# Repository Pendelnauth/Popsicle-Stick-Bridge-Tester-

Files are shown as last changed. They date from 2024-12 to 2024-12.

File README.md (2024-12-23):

# Popsicle Stick Bridge Tester
This is a basic Popsicle Stick Bridge Tester designed for use in a classroom environment.

# Back Story

This project was created to easily test popsicle stick bridges that students created as a part of the curriculum. This allows a safer and more accurate testing method compared to other more traditional methods.

# Project Notes

Because this is a one-off project little effort was put into refining the project. Certain aspects of the project need manual modification to allow for working functionality.
  1. The onboard regulator for the -5V rail only can produce -3.3V due to being fed 3.3v and a misunderstanding in the datasheet. The fix for this was to simply change the resistors to set the output voltage to -3V. Because the -5V rail is used to excite the load cell the output voltage is slightly lower making it more difficult to measure.
  2. ADC 16x gain input impedance. Due to the small voltage needed to be measured the internal PGA of the ADC is used to help achieve more stable readings from the load cells. This causes the input impedance of the ADC to drop off rapidly resulting in skewed measurements. To fix this additional oversampling (ADC-based) was applied as well as a rolling average(Program based) while using a lower gain. This kept the visually present noise down to an acceptable level. The preferred solution would be to either use a dedicated buffer or general-purpose amp before the ADC to drive it even at the lower input impedances adequately. Or make use of a purpose-built load cell measurement IC. 

Make sure to check out the User Manual for additional information and operation instructions.

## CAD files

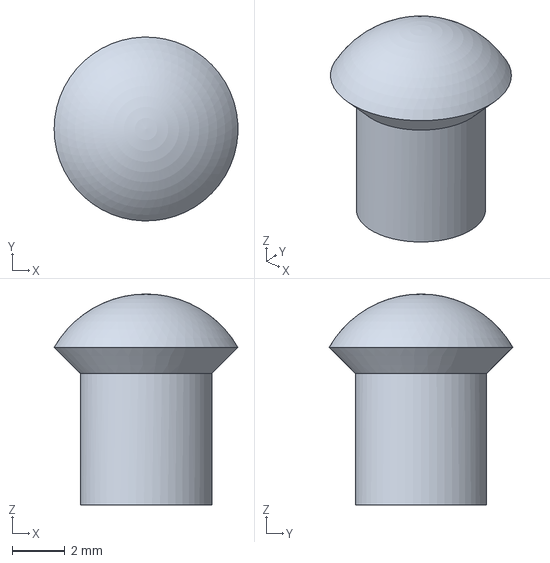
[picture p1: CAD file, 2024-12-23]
MCAD/Top Cover.FCStd
6.99 x 7.00 x 8.03 mm

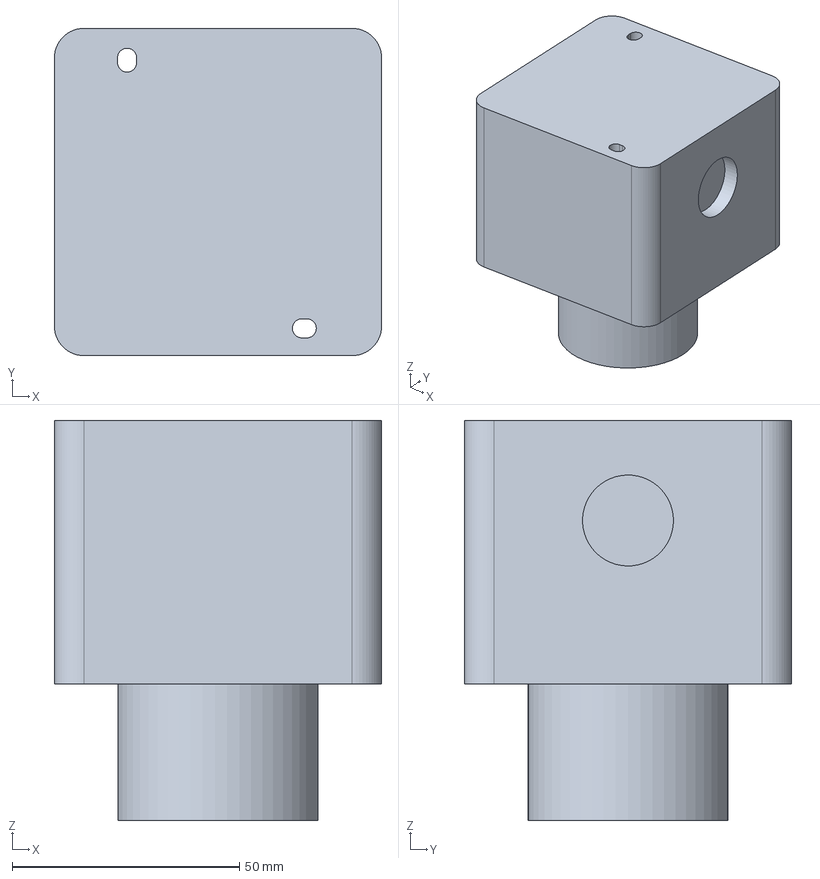
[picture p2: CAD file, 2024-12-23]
MCAD/E-STOP.FCStd
72.0 x 72.0 x 88.0 mm

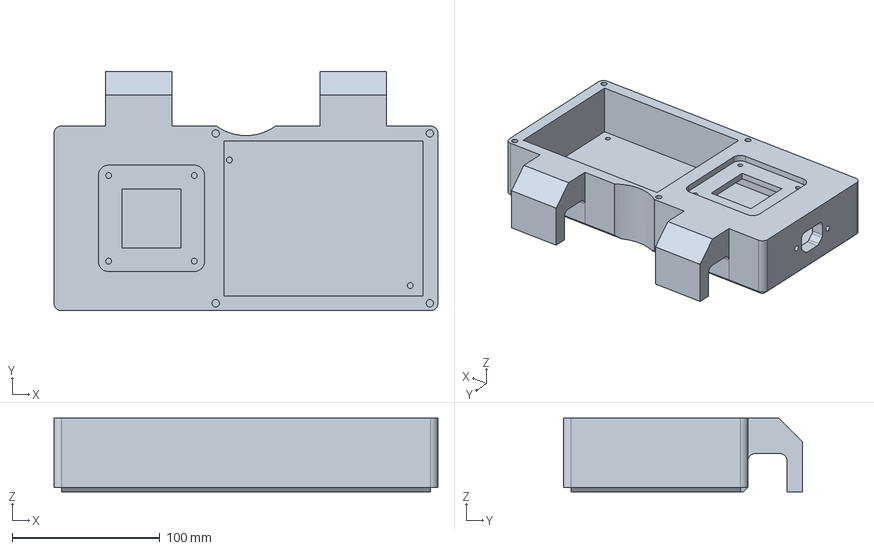
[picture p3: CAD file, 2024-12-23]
MCAD/Bottom Plate.FCStd
260.0 x 162.0 x 50.0 mm

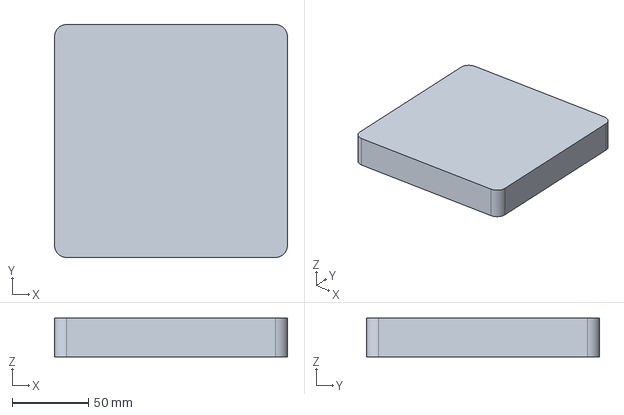
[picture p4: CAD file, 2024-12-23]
MCAD/Spacer Plate.FCStd
152.4 x 152.4 x 25.4 mm

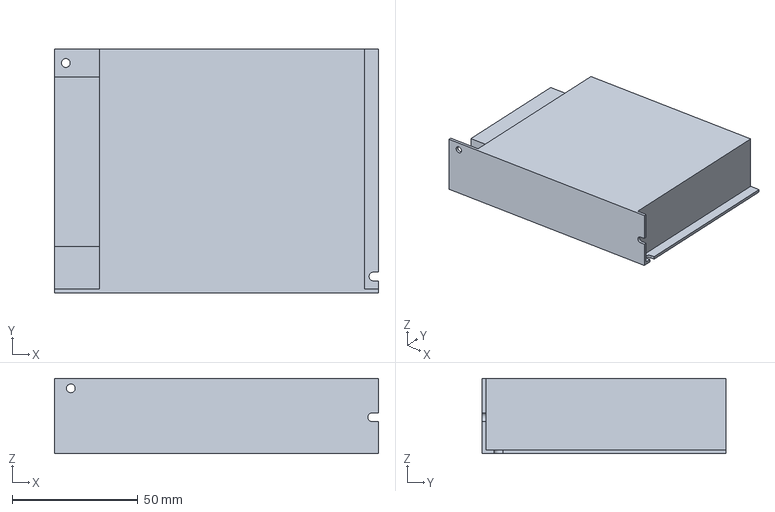
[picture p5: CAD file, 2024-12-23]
MCAD/Power Supply.FCStd
129.0 x 97.0 x 30.0 mm

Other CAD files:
MCAD/Bridge Tester ASM.FCStd

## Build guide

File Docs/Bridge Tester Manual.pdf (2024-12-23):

# Bridge Tester Operator’s Manual

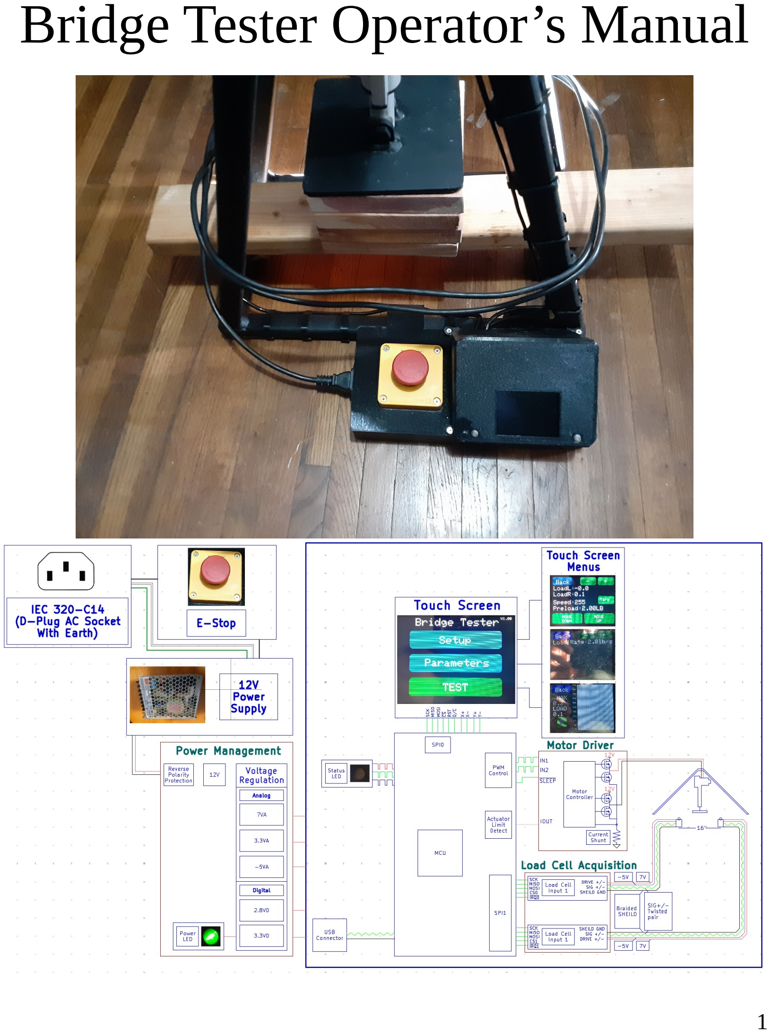
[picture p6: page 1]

1

# Table of contents

# 1. Introduction

This bridge tester is a custom device designed to facilitate in measuring the strength and structural integrity of popsicle stick bridges. This tester allows accurate measurements of a bridge's load-bearing capacity with better repeatability and safety compared to traditional methods. The design makes use of a basic resistive color touch screen to setup and start each test. This manual provides

2

guidance on setting up, operating, and maintaining the bridge tester. It includes practical tips and troubleshooting advice to ensure smooth operation.

# 2. System Characteristics

| Min | Typical | Max | Unit | Conditions
Applied Force | 440 | 700 | 880 | lb | @15-30°C
Force Resolution | 0.1 | 1.0 | | lb | @15-30°C
Single Load Cell Rating | 440 | | 528 | lb | @15-30°C
Load Rate | 2 | | 9.9 | lb/s
Bridge Span | 15.9 | 16.00 | 16.1 | In | Depends on span adjustments
Bridge Width | | | 8 | In
Bridge Height | -2 | 6 | 6.25 | In | Min is based on sitting on a flat surface and represents 2 inches below the load cell pillars
Linear Actuator Force | | | 1320 | lb | Vmotor = 12V (Load Cell Protection Disabled)
Linear Actuator Speed | | | 0.18 | In/s | Vmotor = 12V
Load Cell Excitation Voltage | | 10 | | V | System design
Load Cell Output Full Scale | | | 20 | mV | @ Load Cell Excitation 10V
Measured Load Cell Output | 45.000 | 45.455 | 45.909 | μV/lb
Load Cell Sensitivity | | 2 | | mv/V | @15-30°C
Tester Input Voltage | 11 | 12 | 13 | V | @15-30°C
Tester Input Current | | 3.0 | 8.3 | A | 12V
Operating Temperature | 15 | 25 | 30 | °C
Storage Temperature | 0 | | 50 | °C

3

# 3. Operation Instructions

## 3.1 User Interface Design Philosophy

The interface is designed in such a way that keeps everything intuitive* without compromising on functionality. From this a few basic and common principals can be outlined.

*intuition is subjective – results may vary

1. Rounded rectangles with a text overlay indicates a button.
2. Touching a parameter text on screen selects a parameter.
3. To indicate what parameter on a given screen is selected the color will change to green, if the text is no longer selected it will go back to white. (ex a new parameter is selected)
4. To change a parameter first, select then, press the +/- on the top
left to adjust the parameter.
5. To indicate testing the play button on screen turns red. By default
the button is green as the test is not running.
6. The entire interface uses a simple single depth interface for navigation. (See diagram)

## 3.2 Setup

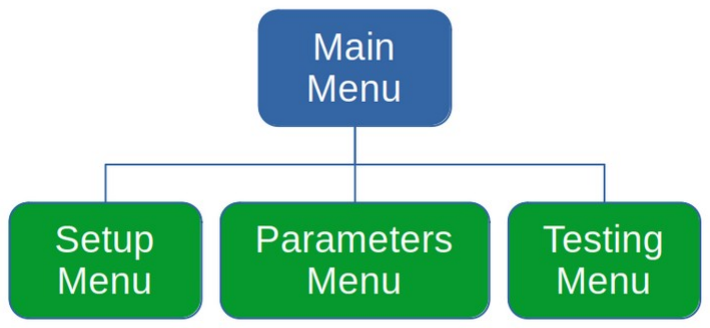
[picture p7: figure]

To begin the tester can be placed in 2 different ways: either placed on a flat surface or positioned so the tester spans a gap between two flat surfaces (ex: 2 tables). The latter method is preferable as it allows more room below the tester for the bridge to extend during testing. This allows the tester to completely finish the test automatically without the tester being lifted by the actuator combined with the extra thickness provided by the bridge.
Ensure the tester is also positioned near a power outlet. Next, plug in and turn on the tester. This can be done by releasing the emergency stop, start by turning the red button clockwise while slightly pushing down until it stops then release. The button should pop up and the tester should turn on and the power LED should light up (arrow shown below). Wait 5-10 seconds and the following should be displayed on the screen.

4

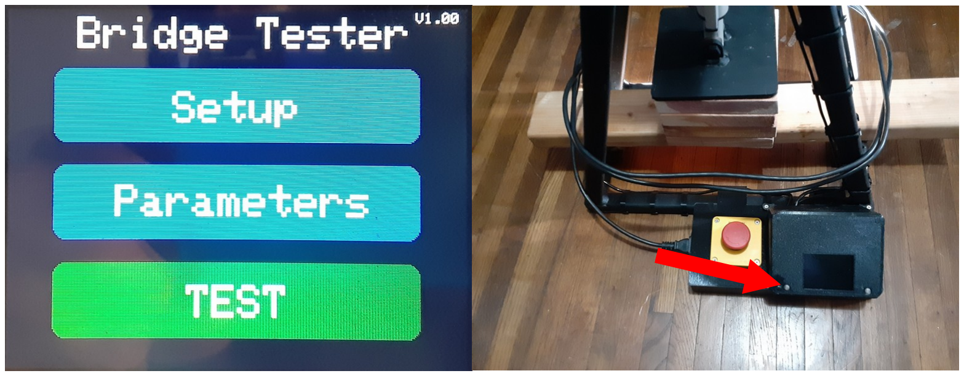
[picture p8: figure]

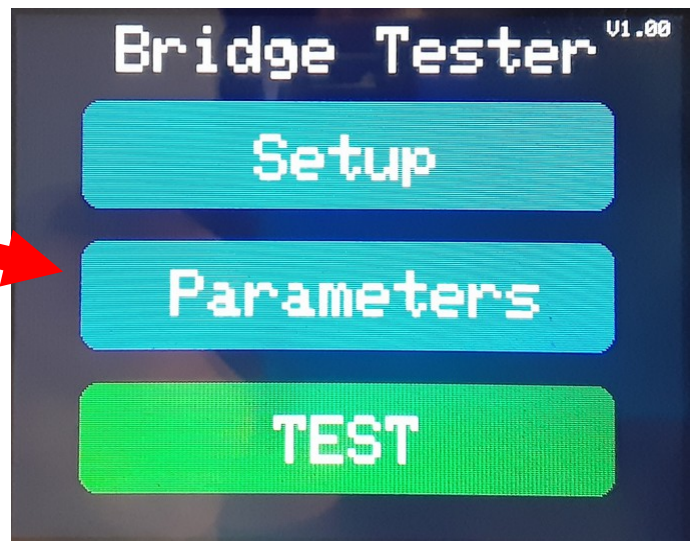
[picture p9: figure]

Select the “Parameters” menu.

Use the “+” and “-” buttons to change to the desired load rate (2 - 9.9 lb/s)

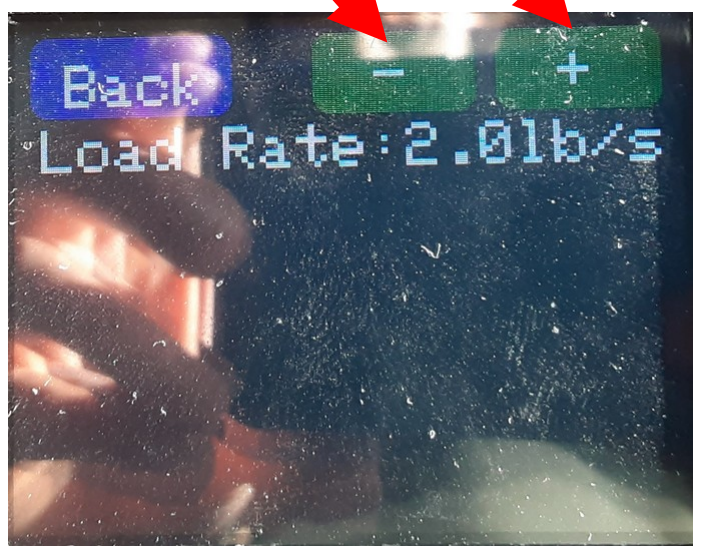
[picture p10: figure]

Select the “Setup” menu

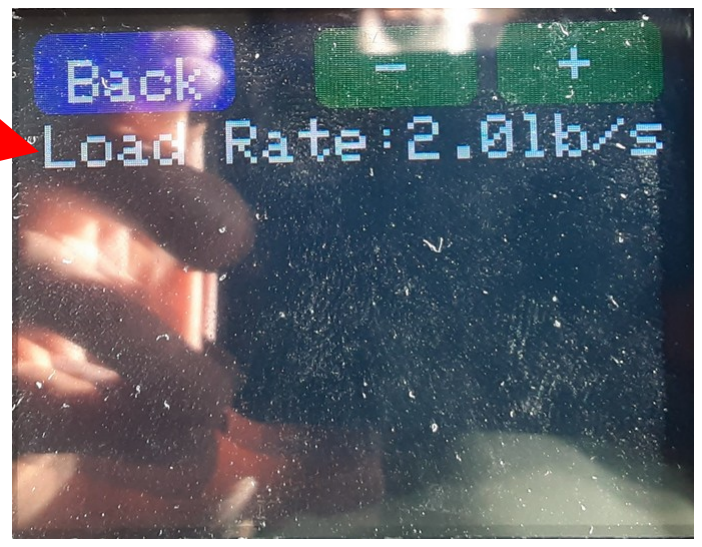
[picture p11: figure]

This will bring up the following. Select “Load Rate:” by pressing on the “Load Rate:” text when selected it will turn green.

To finish simply press “Back” this saves the load rate for future tests even if the tester is powered off.

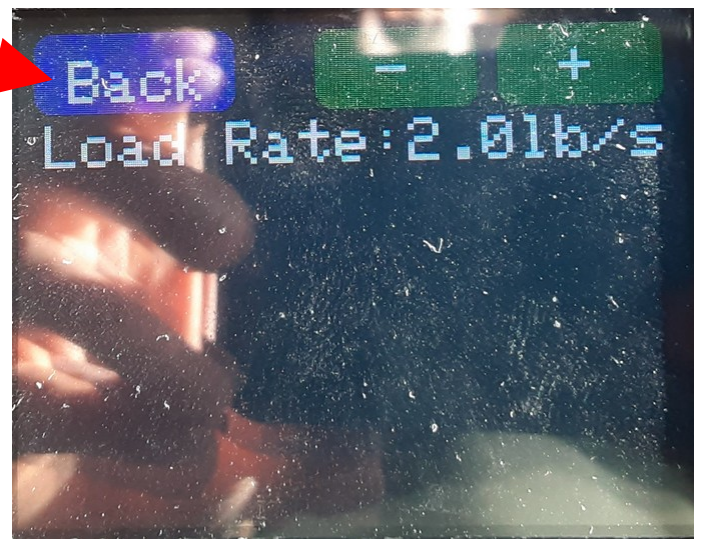
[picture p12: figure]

From here, place the bridge on the tester. If the loading mechanism is too low first raise it using the “Move Down” and “Move Up” buttons. If needed adjust the speed using the “+” and “-” buttons.

5

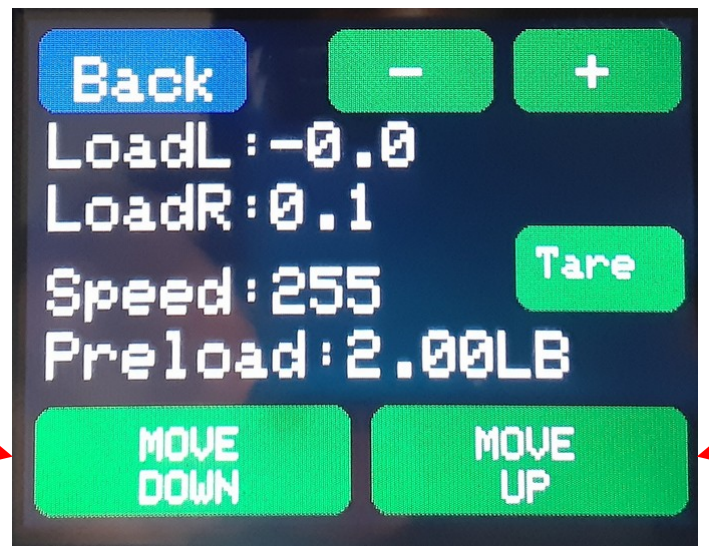
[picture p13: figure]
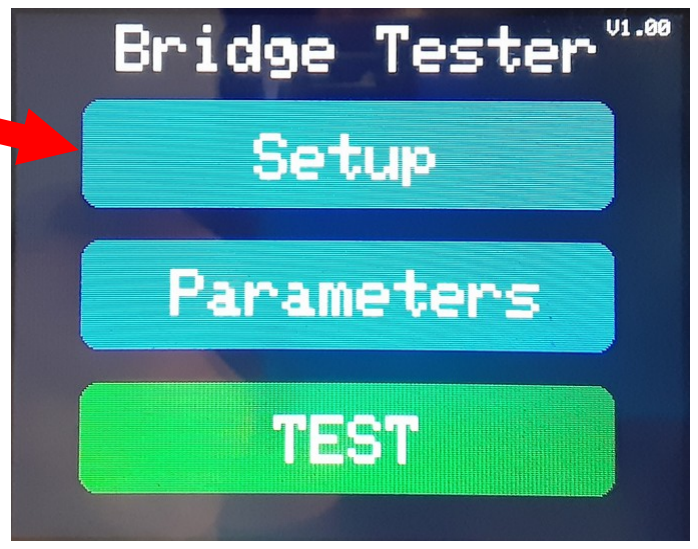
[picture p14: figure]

Select “Preload” and adjust this value to your desired value (0-20lb). Note preload is the starting load that gets applied to the bridge before the test begins. Preload is still added to the overall score when testing. A typical value of (2-5lbs) is recommended. This ensures the actuator in later steps remains in the same spot after you release it.

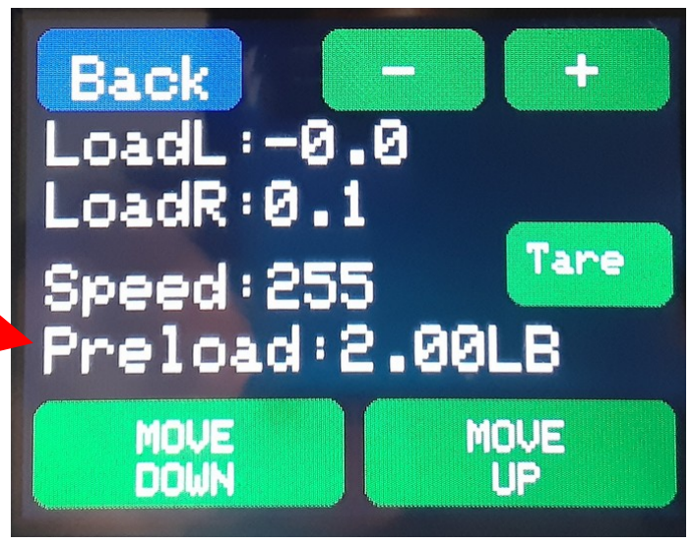
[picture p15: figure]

From here add spacer blocks if the bridge is less than 2” tall and move the actuator down. When you are within ½” of the bridge slow the motor speed to reduce overshoot on the preload. A good value for the speed would be around 50-100. At this point hold the actuator so it is centered and continue moving the actuator down until it stops.

Now without applying any additional force on the bridge press the “Tare” button. This will subtract the weight of the bridge from the final result and “LoadL” and “LoadR” should read near zero.

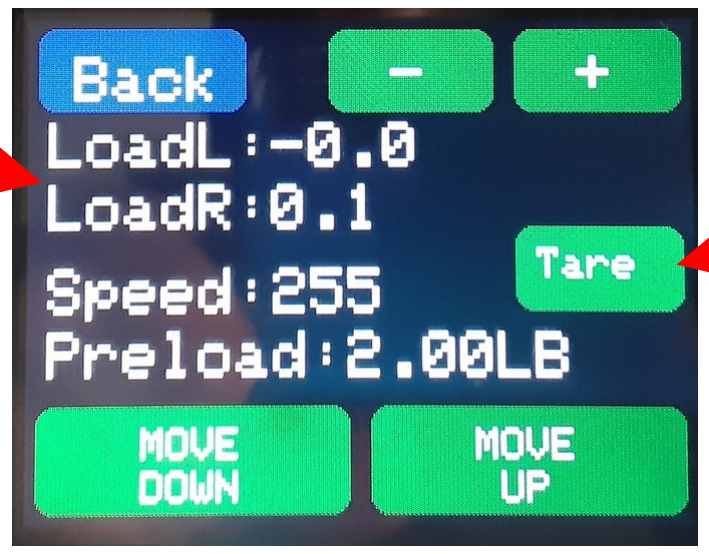
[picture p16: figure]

Once the preload has been reached the actuator will stop moving down. “LoadL” and “LoadR” will display the current force on each side. If a large difference is present you may wish/need to bring the actuator up and re-adjust the left, right balance by slightly tilting the actuator to the side that has the lower reading. Repeat this process until the desired balance is achieved.

6

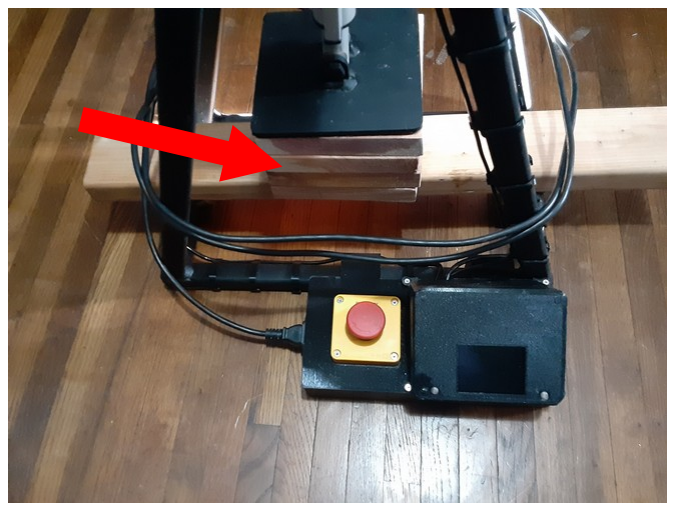
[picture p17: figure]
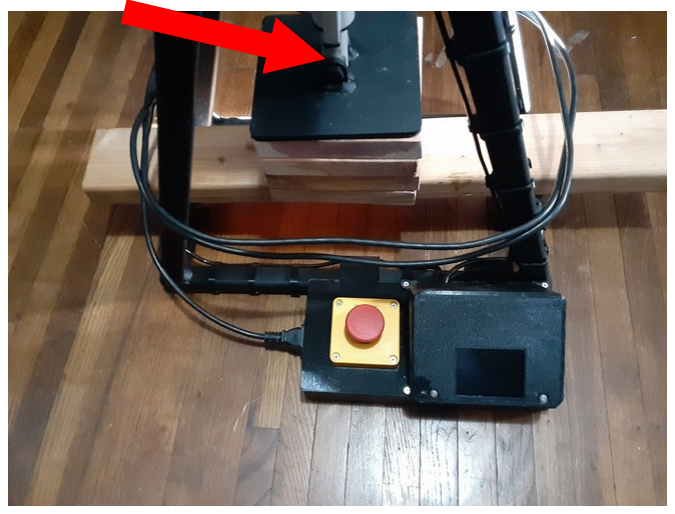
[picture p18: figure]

## 3.3 Testing

Now the tester is all ready to perform a test. Press the “Back” button.

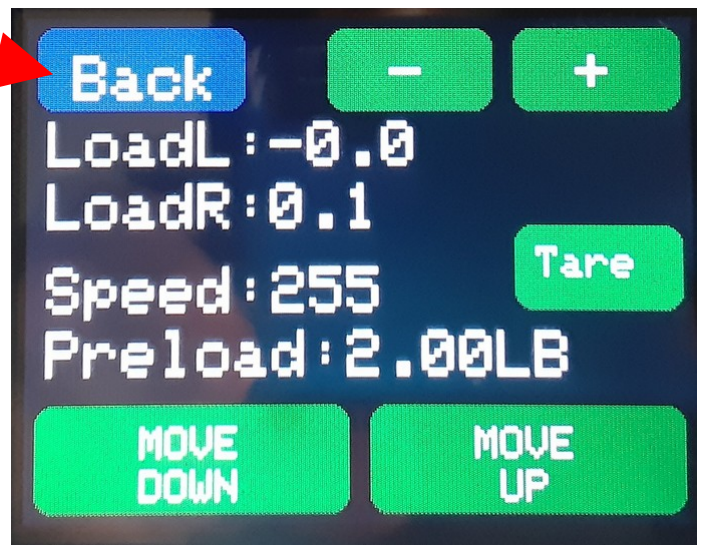
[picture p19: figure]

This will bring up the test menu that displays the max load recorded in pounds, the current load in pounds, and a graph of the load.

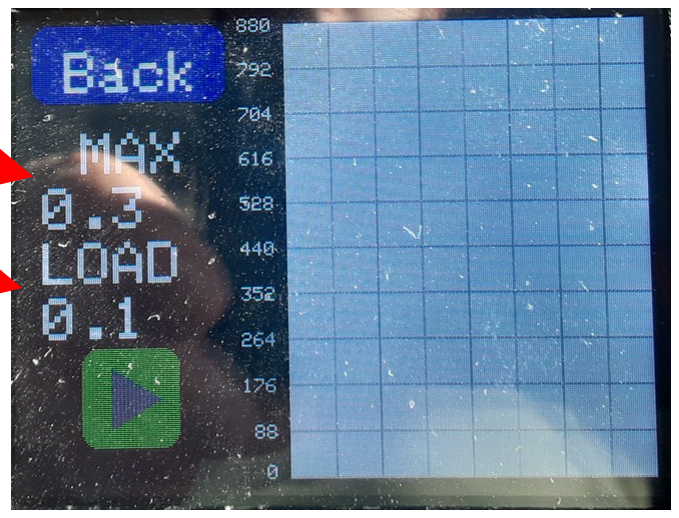
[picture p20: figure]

When the play button is pressed it will turn from green to red to signify that the test is currently running.

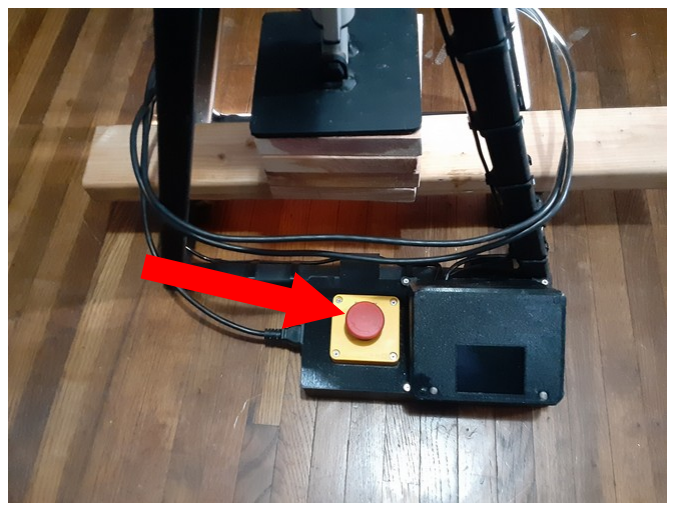
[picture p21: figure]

Testing paused | Testing

Press “TEST”

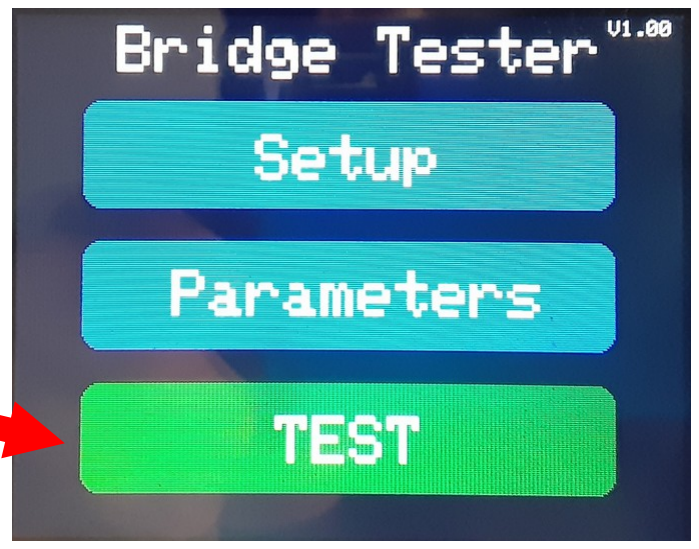
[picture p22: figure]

To start the test press the play button.
Note: The entire area circled can be used to trigger

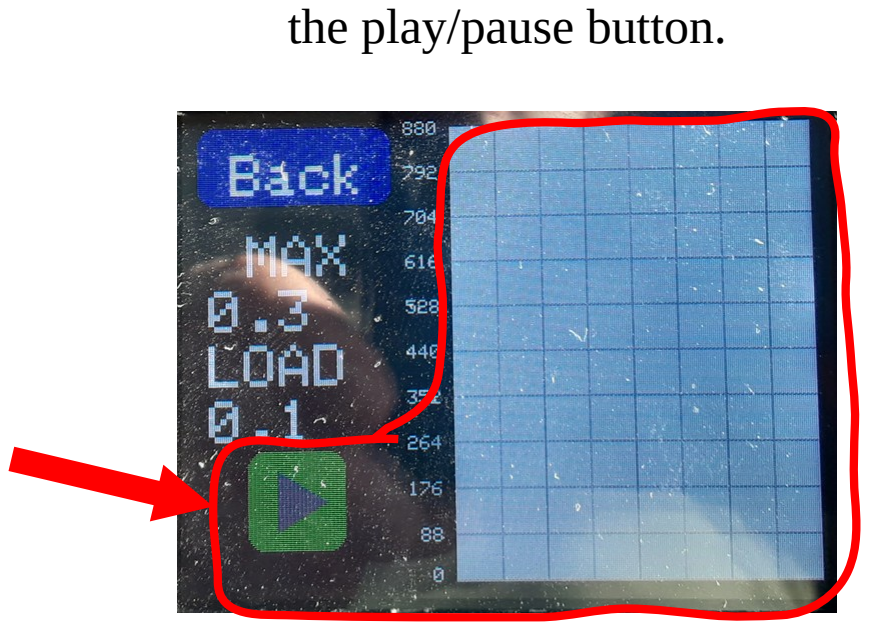
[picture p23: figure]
the play/pause button.

In the event of an emergency simply press down the big red button on the from of the tester. This will remove power from the entirety of the tester.

7

## 3.4 End Testing and System Reset

At the end of the test the actuator will return to the up most position followed by the activation of the status LED (arrow shown below).

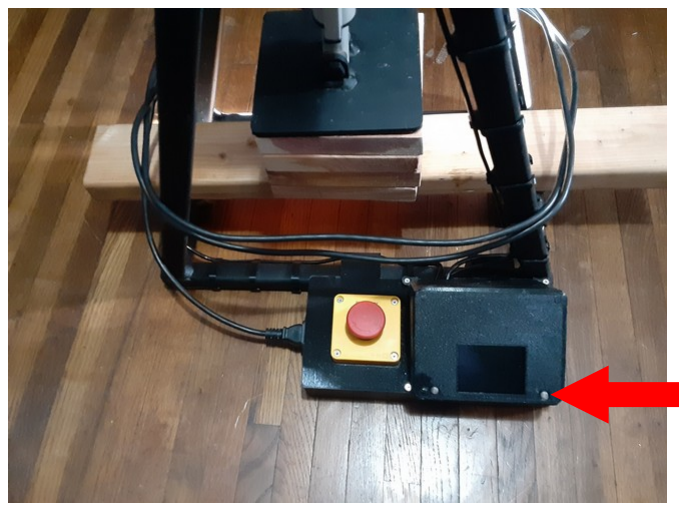
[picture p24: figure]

To reset the tester hold down the play button for at least 5 seconds. This will reset the maximum value and bring you back to the main menu to setup a new test.

If the LED shows Green the test finished without errors. However if the LED shows red this indicates the test ended because one of the load cells reached it’s maximum. If the latter is the case and the max load is less than 880lbs the test may be re-run to try to either break the bridge or obtain a higher score.

Test - Successful | Test - Load Cell Max

8

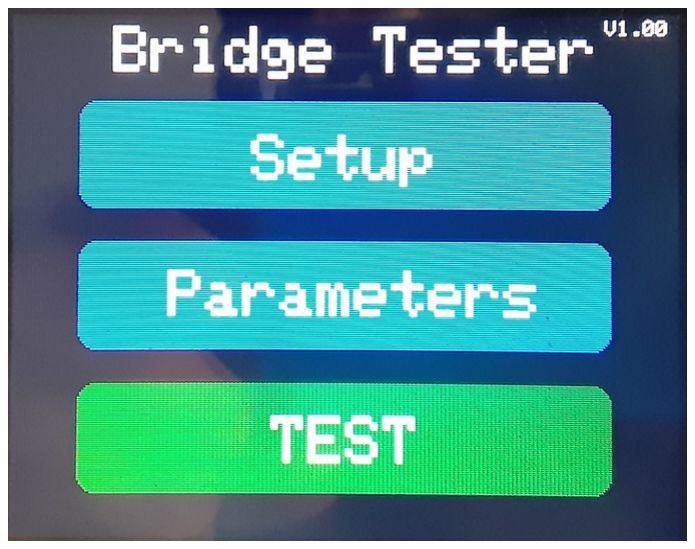
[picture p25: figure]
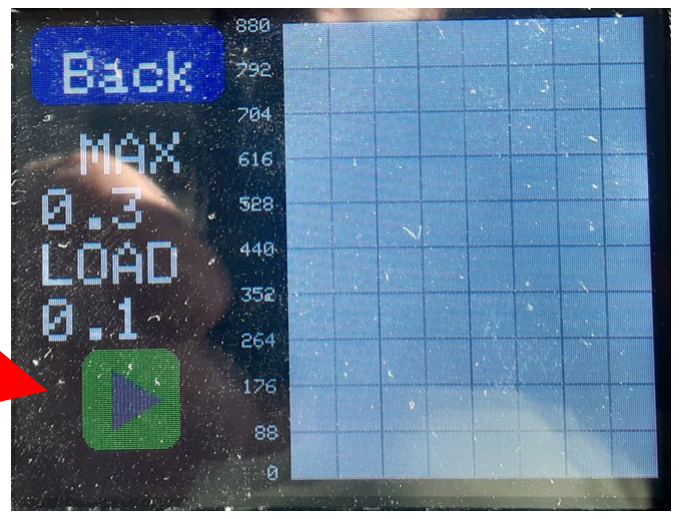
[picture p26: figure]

# 4. Design Info

## 4.1 Electrical

4.11 AC Power Input

The tester takes power from a U.S. standard NEMA 5-15R receptacle. Provided with the tester is a NEMA 5-15P to IEC 320-C13 to make the connection to the tester. The input should be 120V +-10% 60Hz. The side of the electrical enclosure houses a IEC 320-C14 that the included cord can be plugged into. From this connector 3 connections are wired through the enclosure wich includes, earth ground, neutral, and live. Ground and neutral get connected directly to the 12V power supply where as live get connected to the emergency stop switch and then passes to the power supply (see diagram below). This allows all power to be cut to the tester in the event that something goes wrong.

Key:

Green – Earth Ground

White – Neutral

Black – Live

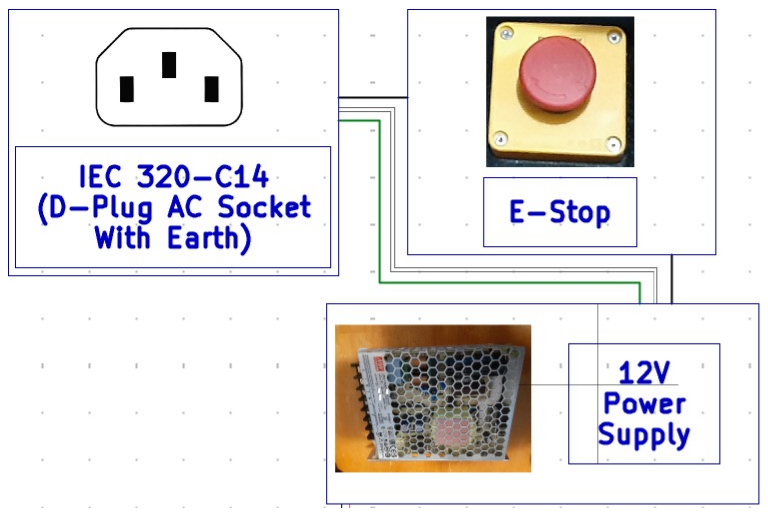
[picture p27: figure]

4.12 Power Supplies

The tester makes use of several power supplies to achieve it’s functionality. This includes 1 off board supply and 5 on board supplies. The main power supply is a 12V 8.4A industry standard 1U power supply. This provides power for the linear

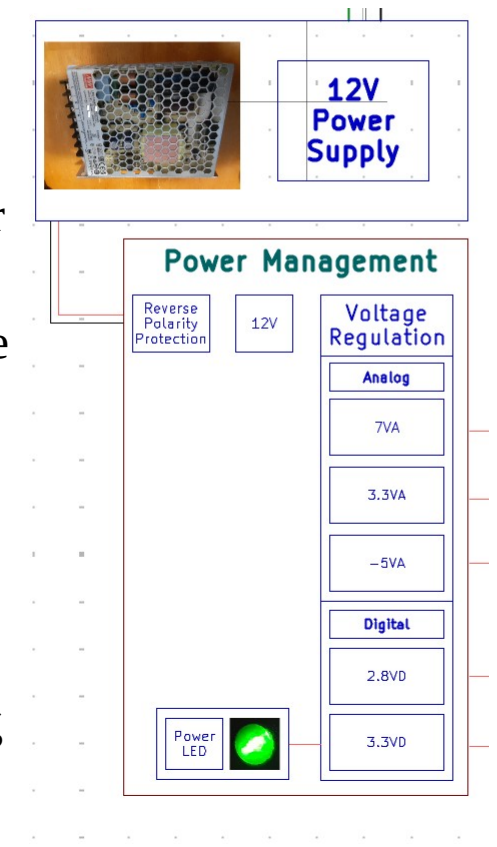
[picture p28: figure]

actuator as well as all subsequent power supplies. From here a switching regulator takes the 12V and outputs 3.3VD for the MCU, Motor Driver, and ADCs(Digital only). This is treated as a dedicated digital supply to help reduce any noise that the digital parts kick back onto the power rail. Also from the 12V rail 7VA is generated using a linear regulator. This supply is solely used as a pre-regulation stage to some of the other regulators and as a bias supply for the load cells. From the 7VA rail 2 supplies are derived 2.8VD and 3.3VA. 2.8V is used by the LCD for some internal function where as the 3.3VA powers the analog section of the ADC. From the 3.3VA rail a -5VA rail is generated also for the function of biasing the load cell. 7V and -5V combined were chosen to allow the ADC’s input to stay within the common mode input requirements which is -0.3 – AVDD + 0.3. In

9

addition the two voltages also total the maximum voltage rating of the load cell of (7 + |-5| = 12V) making measurement slightly better. The load cell forms a whetstone bridge that nominally divides the voltage applied across by 2. This means that the voltage midpoint is around 1V and is within the ADC required specifications. It should be noted that the -5V rail got changed to -3.3V due to a misunderstanding in a data sheet. This still keeps the midpoint at 1.85V so it is still within range however this reduces the overall applied voltage by 1.7V so the load cell outputs a even smaller reading over the entire span (reduced by 3.4mV).

4.13 MCU

At the center of the tester is a RP2040 with 16MIB of on board flash memory. This MCU controls everything from the ADCs to the Motor controller, and touch screen. The RP2040 is a dual core ARM Cortex-M0+ @ 133Mhz with 264kiB of RAM. This MCU was chosen for its good IO, peripherals, speed, and cost. Key features include USB support for direct program upload without the need for a self developed boot loader.

4.14 HID

A single 320x480 RGB resistive touch screen was used for it’s feasibility as well as it’s low cost. This allows for very little planning on the interface side in the early stages of the project as all buttons use the touch screen. Additionally 2 LEDs are also provided to indicate power and testing status.

4.15 Motor Driver

The motor driver manages the 4 N-Channel MOSFETs in a H-bridge configuration. This includes an in integrated charge pump, Fet drivers, and Current shunt amplifier. The FETs were chosen to have a low RDSon and reasonable gate charge to allow for favorable static and switching characteristics. The shunt amplifier is particularly nice as it allows the controller to detect when the limit switch for the motor has been triggered without needing a separate amplifier to be designed for this function.

4.16 Load Cells

The load cells for this tester have the ability to measure up to 200kg(440lbs) each meaning that the total force applied can be 400kg(880lbs). They have an output of 20mv/V (full span) meaning if 200kg were applied to the load cell and 1V was applied the load cell would measure 20mv. The maximum voltage allowable is 12V meaning that each lb is about 54μV(MAX). To measure this small voltage serval techniques are used to get good results. First a 24bit ADC is used this allows for direct measurement as with a 3.3V reference each LSB is about 197nV far lower than the needed increment. The chosen ADC the MCP3561RT-E/ST has additional features including a programmable gain amplifier and automatic oversampling to help aid in the measurement. Additionally in software a rolling average is applied to

10 the samples to improve consistency reducing jitter. If the system was to go though a second revision It would be good to place a LNA in between the load cell and the ADC to better drive the ADC. This would help to reduce the offset caused by the relatively low input impedance of the ADC.

## 4.2 Software

4.21 Libraries

SPI.h – Used for easy acess to the the on chip spi hardwear for LCD and ADC communication.

Adafruit_GFX.h – Contains basic graphics functions like drawing text and other objects on a screen.

Adafruit_ILI9341.h – Basic driver for the LCD driver IC.

SingleFileDrive.h – Makes use of the on board USB port to enumerate as a usb flash drive with a single file was going to be used for data output but was removed (not used)

LittleFS.h – A high reliability file system for embedded applications that has power loss protections. This gets used for storing parameters within a dedicated section of the program memory.

EEPROM.h – Interfaces with littlefs and the on board flash to write to a dedicated address as if it was an internal EEPROM on chip. Used for storing settings set by the user.

pico/mutex.h – A basic mutex from the RPI SDK. This allows safe access to a singe memory address to both of the 2 cores on the RP2040 ensuring that both cores do not try to read or write from the same address at the same cycle.

PID_v1.h – A quality PID implementation originally it was going to be used for the load rate control loop but proved to be more work that it was worth to tune the parameters and get a better result.(not used)

Rpi_Pico_TimerInterrupt.h – A breakout of the internal timer interrupts from the rp2040 (not used)

4.22 Functions

ADC_Take_Reading – Starts and waits for an ADC conversion to occur for both of the load cells.

Get_ADC_Register – Takes in what ADC you wish to read from as well as the register address number.

ADC_Read_Value0 – Call at the end of each read interrupt call from a ADC0.

11

ADC_Read_Value1 – Call at the end of each read interrupt call from a ADC1.

SPI_Restart – Restarts the SPI Interface.

Start_Motor – This changes the state of the NSLEEP pin so the motor controller is taken out of sleep mode and allowed to run the motor.

Update_Motor - This writes the current motor speed value and direction to the controller and makes the motor move as directed.

Stop_Motor – This puts the motor controller in sleep mode so that the motor can no longer run.

Motor_Current – Gets the current motor current measured by the internal amplifier and external shunt amplifier.

Main_Menu – Houses all the code used to run the logic for the main menu.

Setup_Menu - Houses all the code used to run the logic for the setup menu.

Test_Menu - Houses all the code used to run the logic for the test menu.

Parameters_Menu - Houses all the code used to run the logic for the parameters menu.

Touch_Screen_Sample_x – This function handles the measurement of the x coordinate of the touch screen this includes any averaging that might be needed to get good results.

Touch_Screen_Sample_y - This function handles the measurement of the y coordinate of the touch screen this includes any averaging that might be needed to get good results.

Check_Box_Touch – Creates a touch rectangle bounded area that can be used to act an input for some other function.

4.23 Uploading Programs

Uploading programs to the RP2040 is very easy and can be done in 2 ways. Using method 1 required a bit more work to start out but offers the ability to make code changes as well as not needing to remove the top electrical cover of the bridge tester.

12

1. Using Arduino IDE. First start by downloading and installing Arduino IDE. Then open up Arduino IDE going to file → Prefrences → Additional Board Manager URLs and pase in “https://github.com/earlephilhower/arduino-pico/releases/download/global/package_rp2040_index.json”. (https://github.com/earlephilhower/arduino-pico/releases/download/global/package_rp2040_index.json) From here click OK. Go to Tools → Board → Board Manager. Type in “pico”. Select install on the library that says “by Earle F. Philhower, III”. Wait for the process to finish. Go to Tools → Board → Raspberry Pi Pico/RP2040 Generic RP2040. From here go back to Tools and make sure that the settings shown in the Red box are set the same as in the picture. From here plug in the tester using a usb-C cable. Arduino should auto select the board but if not click the drop down box at the top of the screen before the tool bar and select the RP2040. From here simply click the arrow button circled in Green in the picture. The program has just been uploaded as long as no errors popped up.

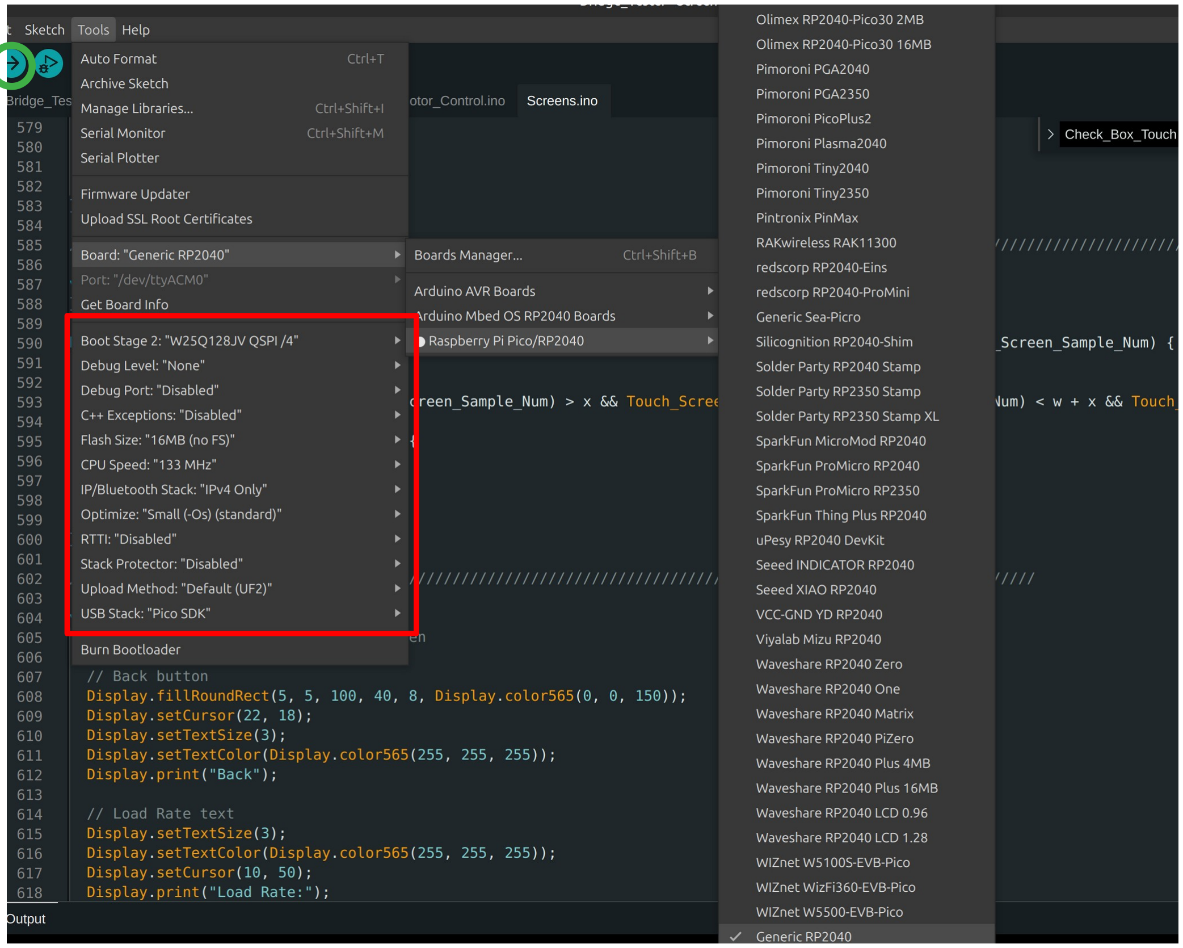
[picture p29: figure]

13

2. Using a pre-compiled .UF2 file. Start by removing the top electrical cover from the Bridge Tester. Locate the Reset and Boot Select Buttons. Plug in your USB-C Cable to your computer and the tester. Now hold down the boot select button and briefly press the reset button. Finally stop pressing the boot select button. At this time you should be able to see the RP2040 on your computer as a USB flash drive. Simply drag the UF2 file onto the RP2040 USB drive and wait for it to disconnect. Once it disconnects the programming process is complete.

# 5. Definitions

ADC – Analog to Digital Converter HID – Human Interface Device LCD – Liquid Crystal Display LNA – Low Noise Amplifier
LSB – Least Significant Bit MCU - Micro Controller Unit PID – Proportional Integral Control RPI – Raspberry PI
SDK – Software Development Kit

14

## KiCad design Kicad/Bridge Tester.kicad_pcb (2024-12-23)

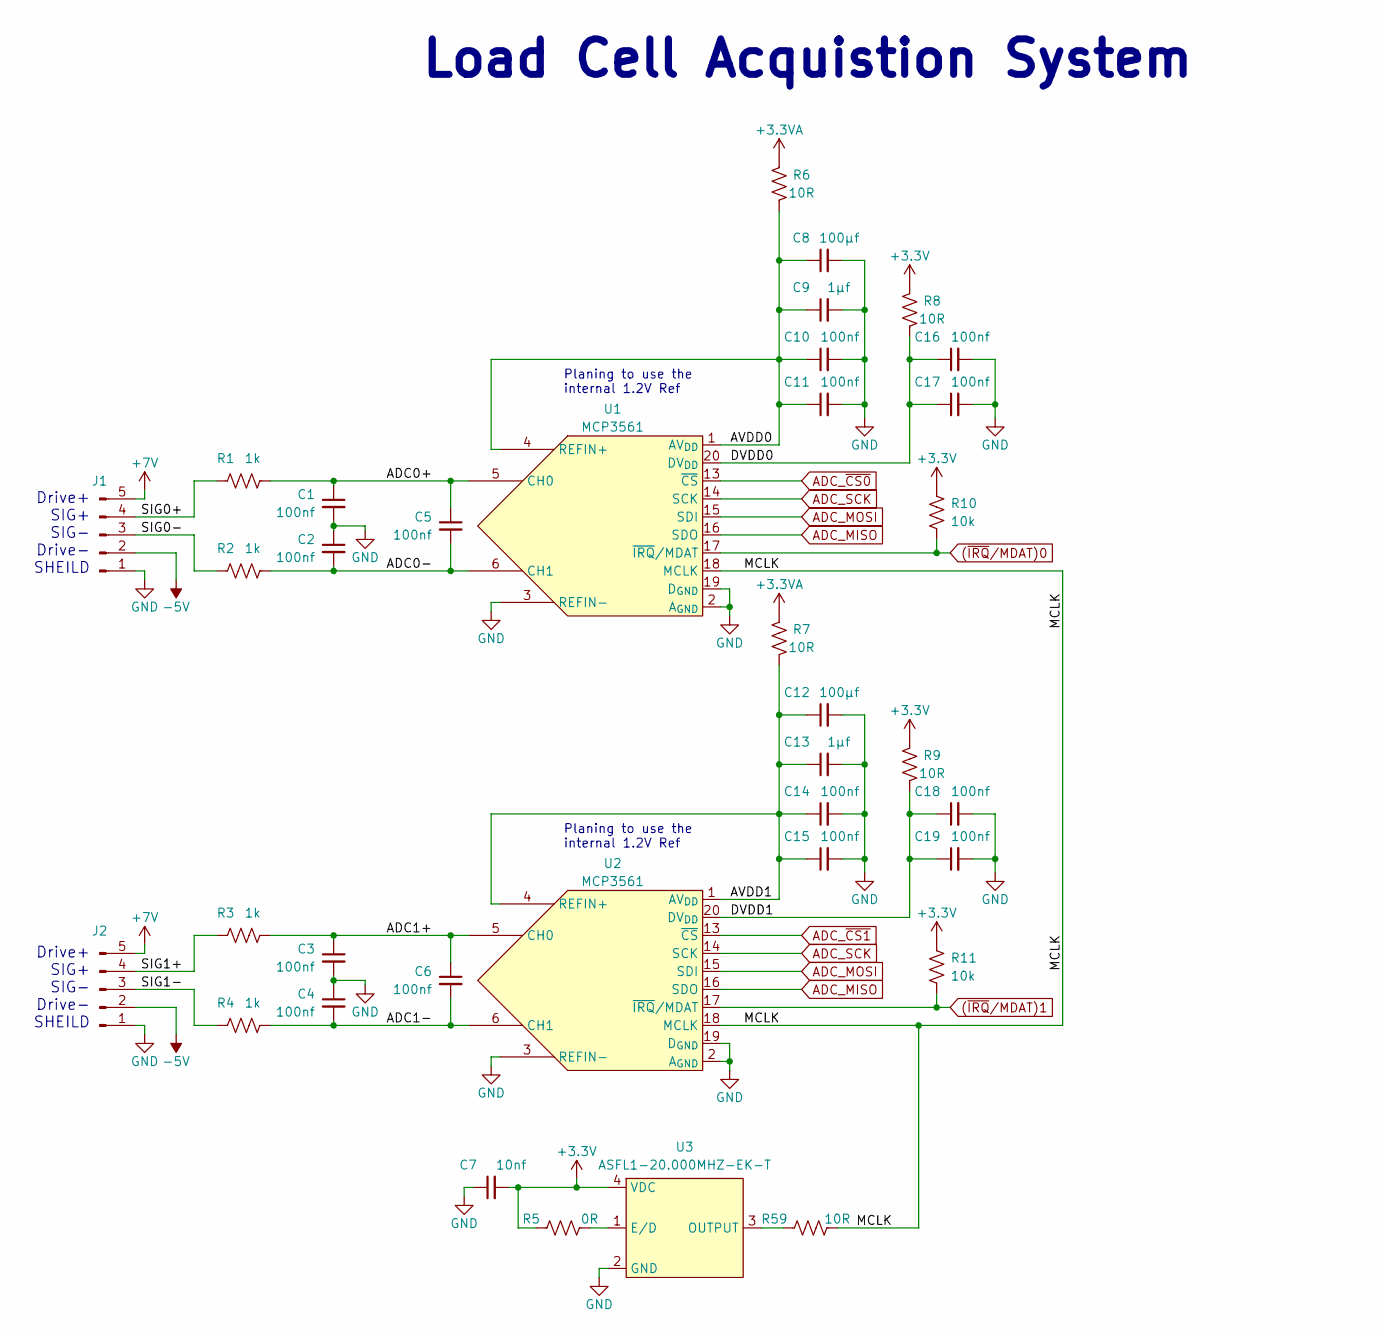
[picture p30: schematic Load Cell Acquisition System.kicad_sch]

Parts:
C1, C2, C3, C4, C5, C6, C10, C11, C14, C15, C16, C17, C18, C19: 100nf; C_0603_1608Metric
C7: 10nf; C_0603_1608Metric
C8, C12: 100μf; C_1206_3216Metric
C9, C13: 1μf; C_0603_1608Metric
J1, J2: Conn_01x05_Pin; JST_PH_B5B-PH-K_1x05_P2.00mm_Vertical
R1, R2, R3, R4: 1k; R_0603_1608Metric
R5: 0R; R_0603_1608Metric
R6, R7, R8, R9, R59: 10R; R_0603_1608Metric
R10, R11: 10k; R_0603_1608Metric
U1, U2: MCP3561; TSSOP-20_4.4x6.5mm_P0.65mm
U3: ASFL1-20.000MHZ-EK-T; 4-SMD

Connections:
(~IRQ/MDAT)0: R10.2, U1.17 (~IRQ/MDAT); also elsewhere on the board
(~IRQ/MDAT)1: R11.2, U2.17 (~IRQ/MDAT); also elsewhere on the board
+3.3V: C7.2, R5.1, R8.2, R9.2, R10.1, R11.1, U3.4 (VDC); also elsewhere on the board
+3.3VA: R6.2, R7.2; also elsewhere on the board
+7V: J1.5, J2.5; also elsewhere on the board
-5V: J1.2, J2.2; also elsewhere on the board
/Load Cell Acquisition System/ADC0+: C1.1, C5.1, R1.2, U1.5 (CH0)
/Load Cell Acquisition System/ADC0-: C2.2, C5.2, R2.2, U1.6 (CH1)
/Load Cell Acquisition System/ADC1+: C3.1, C6.1, R3.2, U2.5 (CH0)
/Load Cell Acquisition System/ADC1-: C4.2, C6.2, R4.2, U2.6 (CH1)
/Load Cell Acquisition System/AVDD0: C8.1, C9.1, C10.1, C11.1, R6.1, U1.1 (AV_{DD}), U1.4 (REFIN+)
/Load Cell Acquisition System/AVDD1: C12.1, C13.1, C14.1, C15.1, R7.1, U2.1 (AV_{DD}), U2.4 (REFIN+)
/Load Cell Acquisition System/DVDD0: C16.1, C17.1, R8.1, U1.20 (DV_{DD})
/Load Cell Acquisition System/DVDD1: C18.1, C19.1, R9.1, U2.20 (DV_{DD})
/Load Cell Acquisition System/MCLK: R59.2, U1.18 (MCLK), U2.18 (MCLK)
/Load Cell Acquisition System/SIG0+: J1.4, R1.1
/Load Cell Acquisition System/SIG0-: J1.3, R2.1
/Load Cell Acquisition System/SIG1+: J2.4, R3.1
/Load Cell Acquisition System/SIG1-: J2.3, R4.1
ADC_MISO: U1.16 (SDO), U2.16 (SDO); also elsewhere on the board
ADC_MOSI: U1.15 (SDI), U2.15 (SDI); also elsewhere on the board
ADC_SCK: U1.14 (SCK), U2.14 (SCK); also elsewhere on the board
ADC_~CS0: U1.13 (~CS); also elsewhere on the board
ADC_~CS1: U2.13 (~CS); also elsewhere on the board
GND: C1.2, C2.1, C3.2, C4.1, C7.1, C8.2, C9.2, C10.2, C11.2, C12.2, C13.2, C14.2, C15.2, C16.2, C17.2, C18.2, C19.2, J1.1, J2.1, U1.2 (A_{GND}), U1.3 (REFIN-), U1.19 (D_{GND}), U2.2 (A_{GND}), U2.3 (REFIN-), U2.19 (D_{GND}), U3.2 (GND); also elsewhere on the board
unnamed: R5.2, U3.1 (E/D)
unnamed: R59.1, U3.3 (OUTPUT)

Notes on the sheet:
Planing to use the internal 1.2V Ref
Drive+ SIG+ SIG- Drive- SHEILD
Load Cell Acquistion System

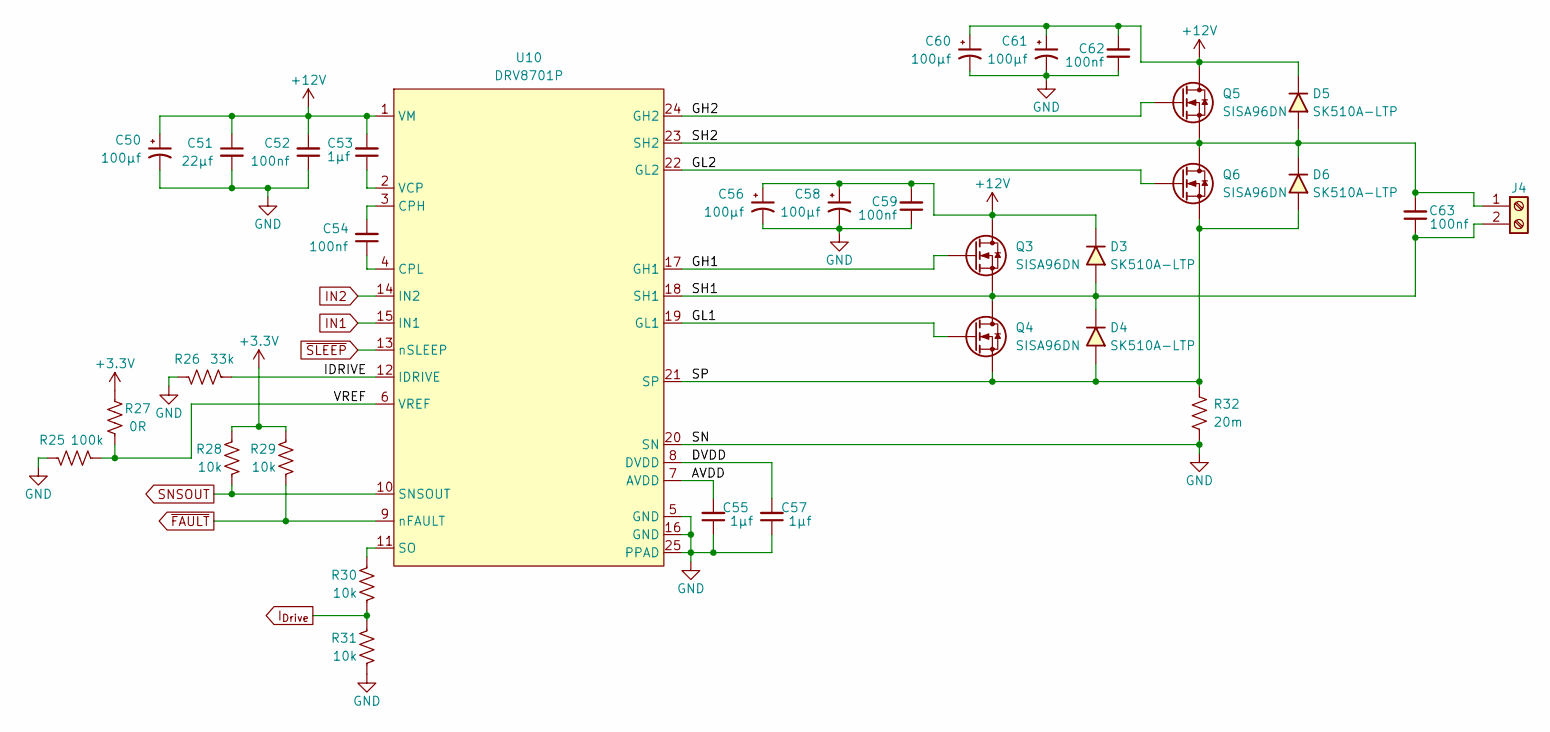
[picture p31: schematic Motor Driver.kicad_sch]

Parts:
C50, C56, C58, C60, C61: 100μf; CP_Elec_6.3x7.7
C51: 22μf; C_0805_2012Metric
C52, C54, C59, C62, C63: 100nf; C_0603_1608Metric
C53, C55, C57: 1μf; C_0603_1608Metric
D3, D4, D5, D6: SK510A-LTP; D_SMA
J4: Screw_Terminal_01x02; YK4410203000G
Q3, Q4, Q5, Q6: SISA96DN; Vishay_PowerPAK_1212-8_Single
R25: 100k; R_0603_1608Metric
R26: 33k; R_0603_1608Metric
R27: 0R; R_0603_1608Metric
R28, R29, R30, R31: 10k; R_0603_1608Metric
R32: 20m; R_2512_6332Metric
U10: DRV8701P; VQFN-24-1EP_4x4mm_P0.5mm_EP2.45x2.45mm_ThermalVias

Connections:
+3.3V: R27.1, R28.1, R29.1; also elsewhere on the board
+12V: C50.1, C51.1, C52.2, C53.2, C56.1, C58.1, C59.2, C60.1, C61.1, C62.2, D3.1 (K), D5.1 (K), Q3.5 (D), Q5.5 (D), U10.1 (VM); also elsewhere on the board
/Motor Driver/AVDD: C55.2, U10.7 (AVDD)
/Motor Driver/DVDD: C57.2, U10.8 (DVDD)
/Motor Driver/GH1: Q3.4 (G), U10.17 (GH1)
/Motor Driver/GH2: Q5.4 (G), U10.24 (GH2)
/Motor Driver/GL1: Q4.4 (G), U10.19 (GL1)
/Motor Driver/GL2: Q6.4 (G), U10.22 (GL2)
/Motor Driver/IDRIVE: R26.1, U10.12 (IDRIVE)
/Motor Driver/SH1: C63.1, D3.2 (A), D4.1 (K), J4.2, Q3.1 (S), Q3.2 (S), Q3.3 (S), Q4.5 (D), U10.18 (SH1)
/Motor Driver/SH2: C63.2, D5.2 (A), D6.1 (K), J4.1, Q5.1 (S), Q5.2 (S), Q5.3 (S), Q6.5 (D), U10.23 (SH2)
/Motor Driver/SP: D4.2 (A), D6.2 (A), Q4.1 (S), Q4.2 (S), Q4.3 (S), Q6.1 (S), Q6.2 (S), Q6.3 (S), R32.1, U10.21 (SP)
/Motor Driver/VREF: R25.1, R27.2, U10.6 (VREF)
GND: C50.2, C51.2, C52.1, C55.1, C56.2, C57.1, C58.2, C59.1, C60.2, C61.2, C62.1, R25.2, R26.2, R31.2, R32.2, U10.5 (GND), U10.16 (GND), U10.20 (SN), U10.25 (PPAD); also elsewhere on the board
IN1: U10.15 (IN1); also elsewhere on the board
IN2: U10.14 (IN2); also elsewhere on the board
I_{Drive}: R30.2, R31.1; also elsewhere on the board
unnamed: C54.2, U10.3 (CPH)
unnamed: C54.1, U10.4 (CPL)
unnamed: R30.1, U10.11 (SO)
unnamed: C53.1, U10.2 (VCP)
SNSOUT: R28.2, U10.10 (SNSOUT); also elsewhere on the board
~FAULT: R29.2, U10.9 (nFAULT); also elsewhere on the board
~SLEEP: U10.13 (nSLEEP); also elsewhere on the board

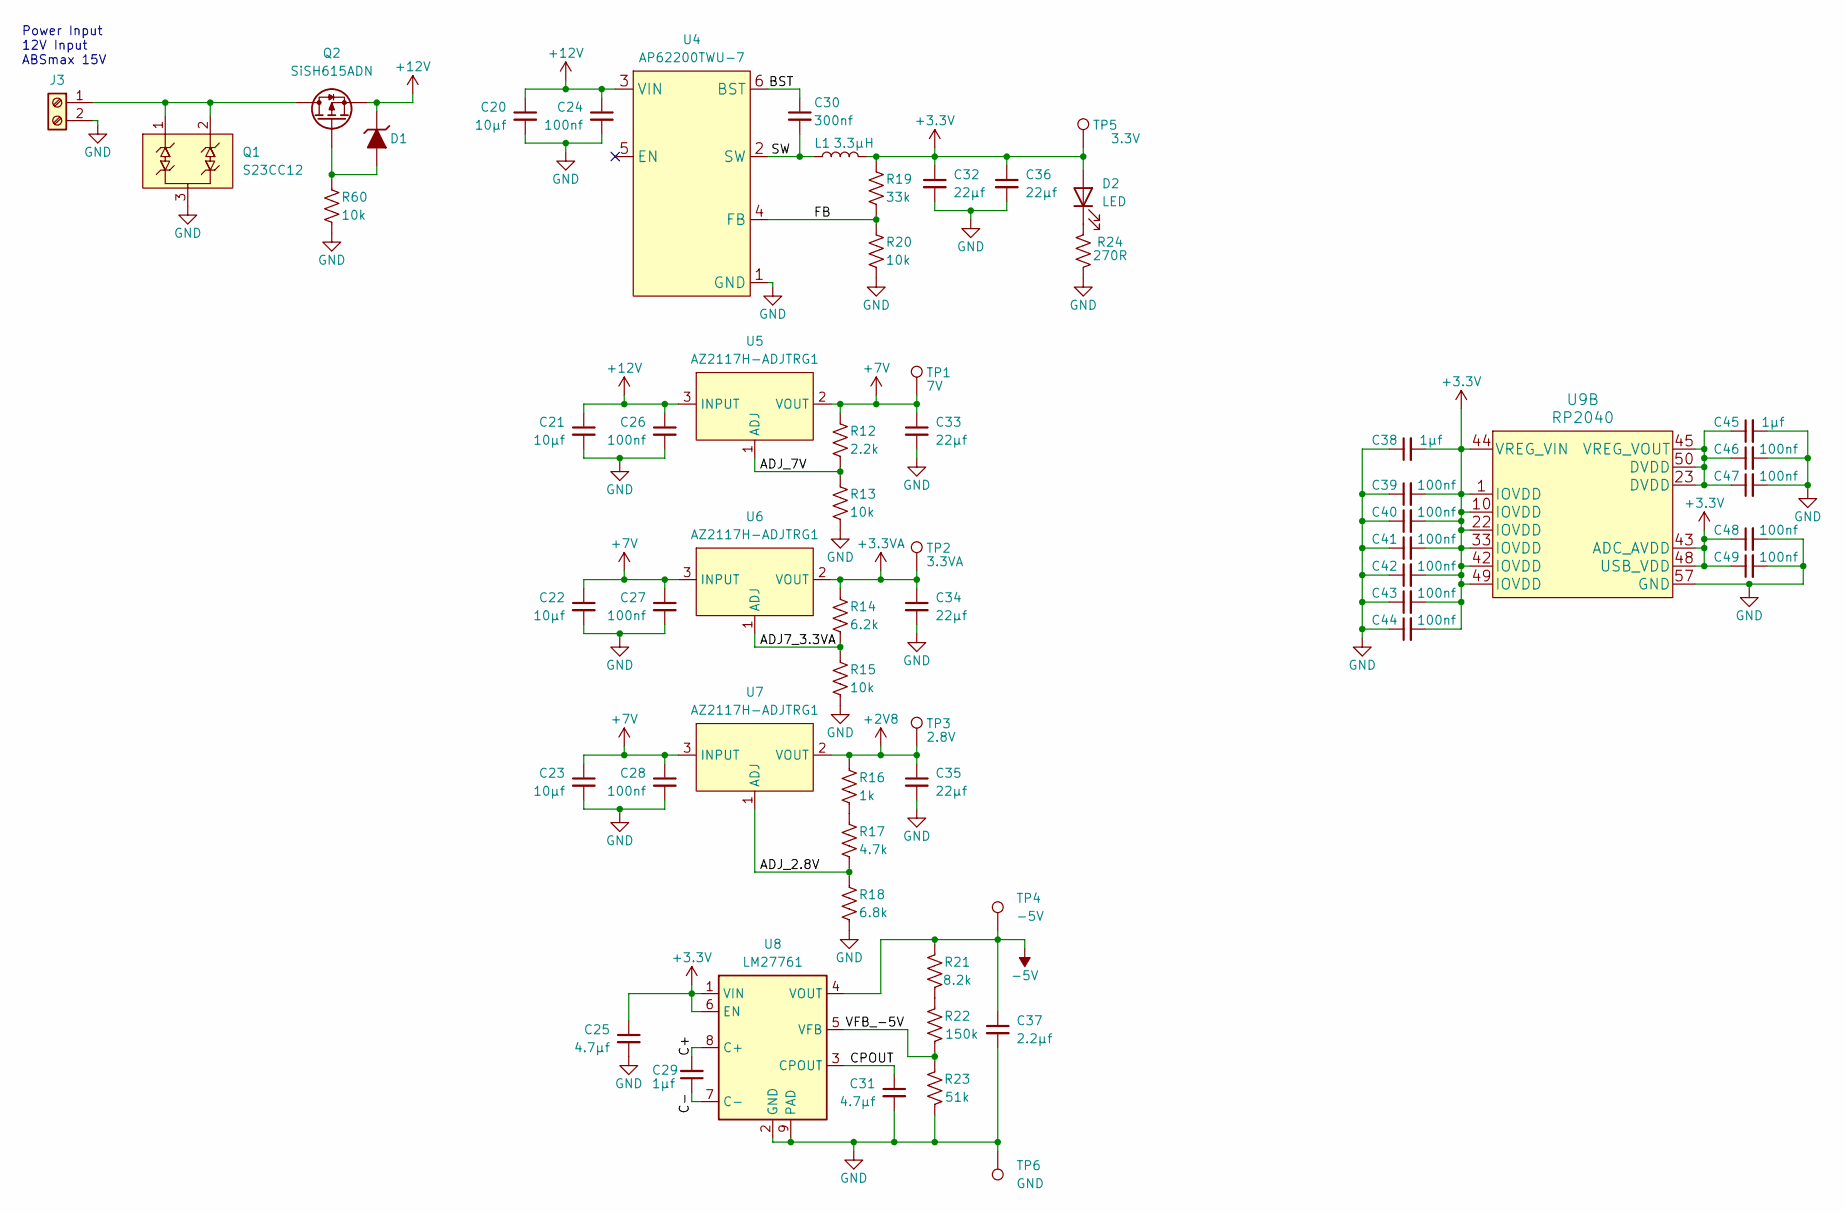
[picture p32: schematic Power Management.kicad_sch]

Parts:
C20, C21, C22, C23: 10μf; C_1206_3216Metric
C24, C26, C27, C28, C39, C40, C41, C42, C43, C44, C46, C47, C48, C49: 100nf; C_0603_1608Metric
C25, C31: 4.7μf; C_0805_2012Metric
C29, C38, C45: 1μf; C_0603_1608Metric
C30: 300nf; C_0603_1608Metric
C32, C33, C34, C35, C36: 22μf; C_0805_2012Metric
C37: 2.2μf; C_0805_2012Metric
D1: MMSZ5240B; D_SOD-123
D2: LED; LED_0603_1608Metric
J3: Screw_Terminal_01x02; YK4410203000G
L1: 3.3μH; APH0630T
Q1: S23CC12; SOT-23-3
Q2: SiSH615ADN; Vishay_PowerPAK_1212-8_Single
R12: 2.2k; R_0603_1608Metric
R13, R15, R20, R60: 10k; R_0603_1608Metric
R14: 6.2k; R_0603_1608Metric
R16: 1k; R_0603_1608Metric
R17: 4.7k; R_0603_1608Metric
R18: 6.8k; R_0603_1608Metric
R19: 33k; R_0603_1608Metric
R21: 8.2k; R_0603_1608Metric
R22: 150k; R_0603_1608Metric
R23: 51k; R_0603_1608Metric
R24: 270R; R_0603_1608Metric
TP1: 7V; TestPoint_Pad_D2.0mm
TP2: 3.3VA; TestPoint_Pad_D2.0mm
TP3: 2.8V; TestPoint_Pad_D2.0mm
TP4: -5V; TestPoint_Pad_D2.0mm
TP5: 3.3V; TestPoint_Pad_D2.0mm
TP6: GND; TestPoint_Pad_D2.0mm
U4: AP62200TWU-7; TSOT-23-6
U5, U6, U7: AZ2117H-ADJTRG1; SOT-223-3_TabPin2
U8: LM27761; WSON-8-1EP_2x2mm_P0.5mm_EP0.9x1.6mm
U9: RP2040

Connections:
+2V8: C35.1, R16.1, TP3.1, U7.2 (VOUT); also elsewhere on the board
+3.3V: C25.1, C32.1, C36.1, C38.2, C39.2, C40.2, C41.2, C42.2, C43.2, C44.2, C48.1, C49.1, D2.2 (A), L1.2, R19.1, TP5.1, U8.1 (VIN), U8.6 (EN), U9.1 (IOVDD), U9.10 (IOVDD), U9.22 (IOVDD), U9.33 (IOVDD), U9.42 (IOVDD), U9.43 (ADC_AVDD), U9.44 (VREG_VIN), U9.48 (USB_VDD), U9.49 (IOVDD); also elsewhere on the board
+3.3VA: C34.1, R14.1, TP2.1, U6.2 (VOUT); also elsewhere on the board
+7V: C22.1, C23.1, C27.1, C28.1, C33.1, R12.1, TP1.1, U5.2 (VOUT), U6.3 (INPUT), U7.3 (INPUT); also elsewhere on the board
+12V: C20.1, C21.1, C24.1, C26.1, D1.1 (K), Q2.1 (S), Q2.2 (S), Q2.3 (S), U4.3 (VIN), U5.3 (INPUT); also elsewhere on the board
-5V: C37.1, R21.2, TP4.1, U8.4 (VOUT); also elsewhere on the board
/Power Management/ADJ7_3.3VA: R14.2, R15.1, U6.1 (ADJ)
/Power Management/ADJ_2.8V: R17.2, R18.1, U7.1 (ADJ)
/Power Management/ADJ_7V: R12.2, R13.1, U5.1 (ADJ)
/Power Management/BST: C30.1, U4.6 (BST)
/Power Management/C+: C29.2, U8.8 (C+)
/Power Management/C-: C29.1, U8.7 (C-)
/Power Management/CPOUT: C31.1, U8.3 (CPOUT)
/Power Management/FB: R19.2, R20.1, U4.4 (FB)
/Power Management/SW: C30.2, L1.1, U4.2 (SW)
/Power Management/VFB_-5V: R22.1, R23.2, U8.5 (VFB)
GND: C20.2, C21.2, C22.2, C23.2, C24.2, C25.2, C26.2, C27.2, C28.2, C31.2, C32.2, C33.2, C34.2, C35.2, C36.2, C37.2, C38.1, C39.1, C40.1, C41.1, C42.1, C43.1, C44.1, C45.2, C46.2, C47.2, C48.2, C49.2, J3.2, Q1.3 (COM), R13.2, R15.2, R18.2, R20.2, R23.1, R24.2, R60.2, TP6.1, U4.1 (GND), U8.2 (GND), U8.9 (PAD), U9.57 (GND); also elsewhere on the board
unnamed: D1.2 (A), Q2.4 (G), R60.1
unnamed: D2.1 (K), R24.1
unnamed: J3.1, Q1.1 (C1), Q1.2 (C2), Q2.5 (D)
unnamed: R16.2, R17.1
unnamed: R21.1, R22.2
unnamed: C45.1, C46.1, C47.1, U9.23 (DVDD), U9.45 (VREG_VOUT), U9.50 (DVDD)

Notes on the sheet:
Power Input 12V Input ABSmax 15V

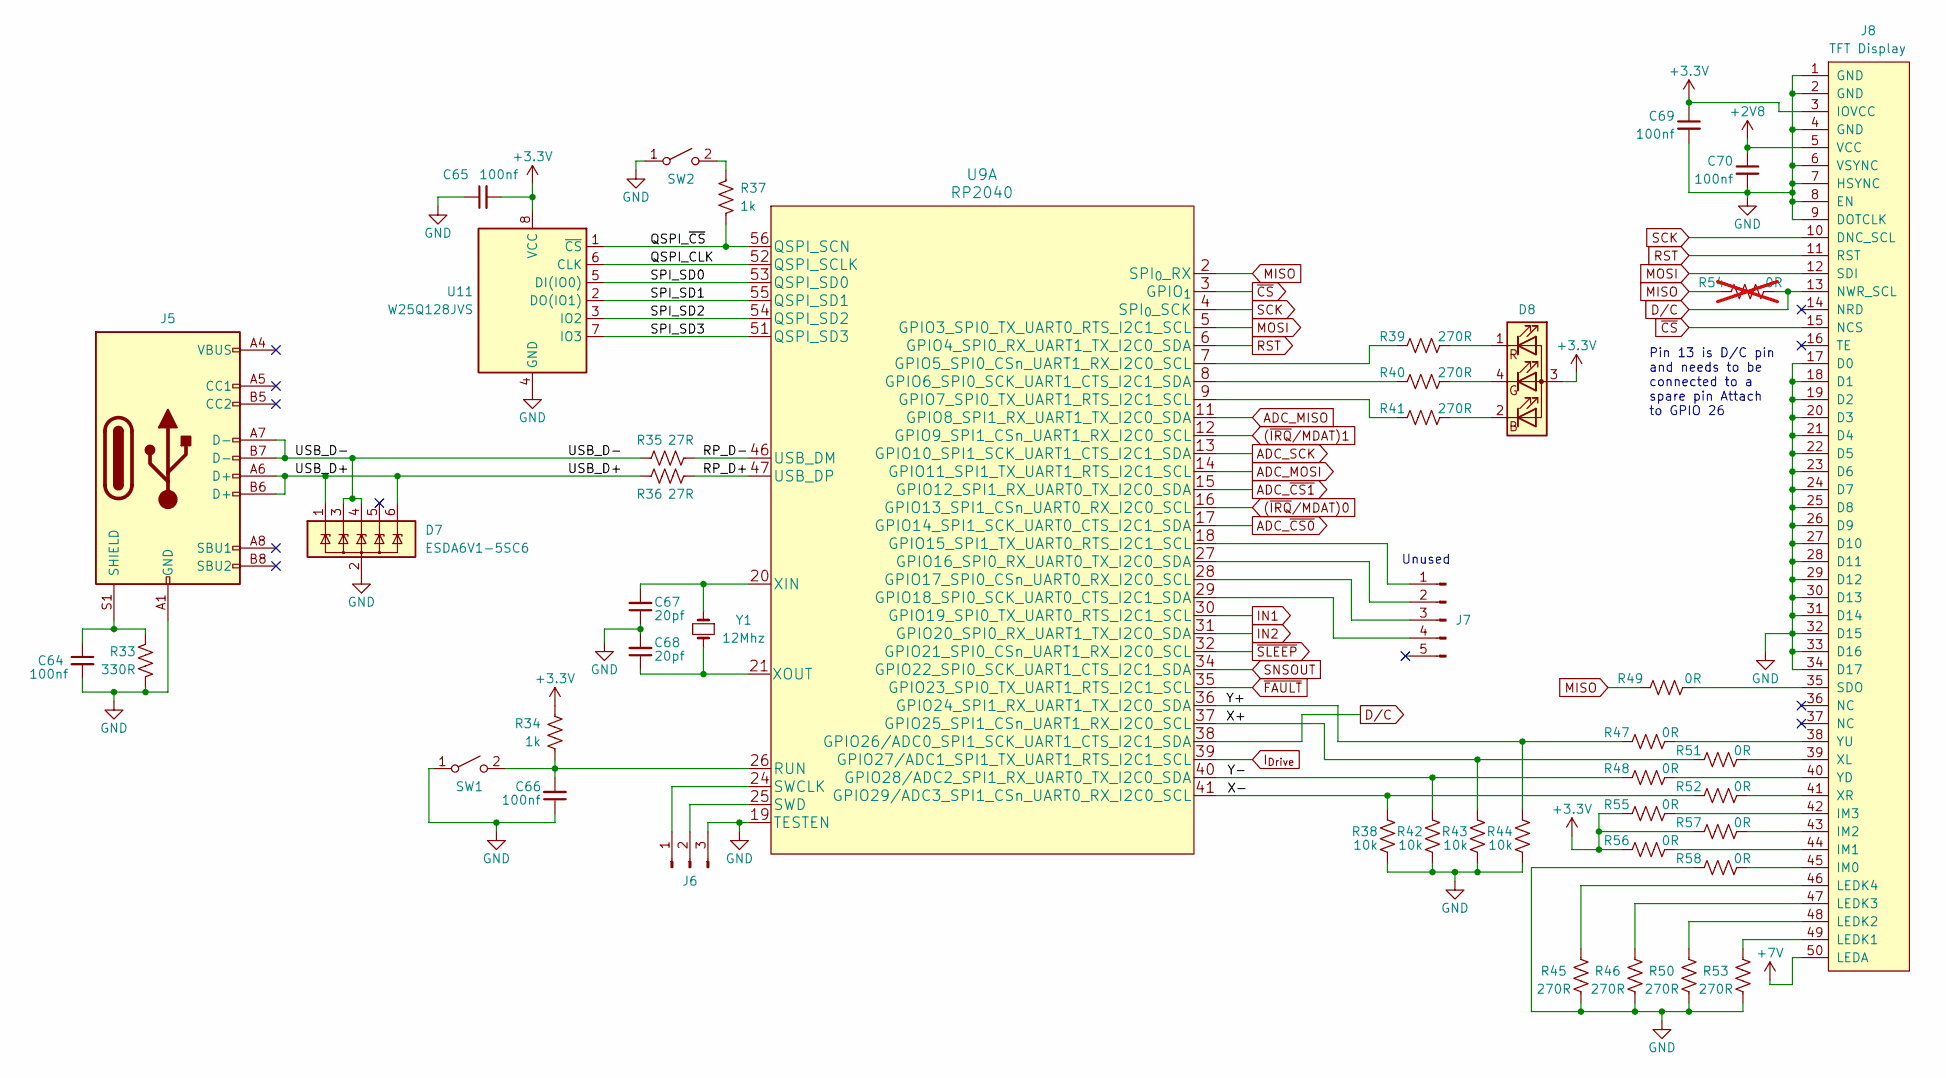
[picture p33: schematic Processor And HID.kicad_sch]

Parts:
C64, C65, C66, C69, C70: 100nf; C_0603_1608Metric
C67, C68: 20pf; C_0603_1608Metric
D7: ESDA6V1-5SC6; SOT-23-6
D8: LED_RBAG; 2.1x2.1 LED
J5: USB_C_Receptacle_USB2.0; USB_C_Receptacle_GCT_USB4105-xx-A_16P_TopMnt_Horizontal
J6: Conn_01x03_Pin; PinHeader_1x03_P2.54mm_Vertical
J7: Conn_01x05_Pin; PinHeader_1x05_P2.54mm_Vertical
J8: TFT Display; MOD-LCD2.8RTP
R33: 330R; R_0603_1608Metric
R34, R37: 1k; R_0603_1608Metric
R35, R36: 27R; R_0603_1608Metric
R38, R42, R43, R44: 10k; R_0603_1608Metric
R39, R40, R41, R45, R46, R50, R53: 270R; R_0603_1608Metric
R47, R48, R49, R51, R52, R55, R56, R57, R58: 0R; R_0603_1608Metric
R54: 0R; R_0603_1608Metric; not fitted
SW1, SW2: SW_SPST; SW_SPST_FSMSM
U9: RP2040
U11: W25Q128JVS; SOIC-8_5.23x5.23mm_P1.27mm
Y1: 12Mhz; Crystal_SMD_HC49-SD

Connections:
(~IRQ/MDAT)0: U9.16 (GPIO13_SPI1_CSn_UART0_RX_I2C0_SCL); also elsewhere on the board
(~IRQ/MDAT)1: U9.12 (GPIO9_SPI1_CSn_UART1_RX_I2C0_SCL); also elsewhere on the board
+2V8: C70.1, J8.5 (VCC); also elsewhere on the board
+3.3V: C65.2, C69.1, D8.3 (A), J8.3 (IOVCC), R34.2, R55.1, R56.1, R57.1, U11.8 (VCC); also elsewhere on the board
+7V: J8.50 (LEDA); also elsewhere on the board
/Processor And HID/QSPI_CLK: U9.52 (QSPI_SCLK), U11.6 (CLK)
/Processor And HID/QSPI_~CS: R37.1, U9.56 (QSPI_SCN), U11.1 (~CS)
/Processor And HID/RP_D+: R36.2, U9.47 (USB_DP)
/Processor And HID/RP_D-: R35.2, U9.46 (USB_DM)
/Processor And HID/SPI_SD0: U9.53 (QSPI_SD0), U11.5 (DI(IO0))
/Processor And HID/SPI_SD1: U9.55 (QSPI_SD1), U11.2 (DO(IO1))
/Processor And HID/SPI_SD2: U9.54 (QSPI_SD2), U11.3 (IO2)
/Processor And HID/SPI_SD3: U9.51 (QSPI_SD3), U11.7 (IO3)
/Processor And HID/USB_D+: D7.1 (IO1), D7.6 (IO5), J5.A6 (D+), J5.B6 (D+), R36.1
/Processor And HID/USB_D-: D7.3 (IO2), D7.4 (IO3), J5.A7 (D-), J5.B7 (D-), R35.1
/Processor And HID/X+: R43.2, R51.1, U9.37 (GPIO25_SPI1_CSn_UART1_RX_I2C0_SCL)
/Processor And HID/X-: R38.2, R52.1, U9.41 (GPIO29/ADC3_SPI1_CSn_UART0_RX_I2C0_SCL)
/Processor And HID/Y+: R44.2, R47.1, U9.36 (GPIO24_SPI1_RX_UART1_TX_I2C0_SDA)
/Processor And HID/Y-: R42.2, R48.1, U9.40 (GPIO28/ADC2_SPI1_RX_UART0_TX_I2C0_SDA)
ADC_MISO: U9.11 (GPIO8_SPI1_RX_UART1_TX_I2C0_SDA); also elsewhere on the board
ADC_MOSI: U9.14 (GPIO11_SPI1_TX_UART1_RTS_I2C1_SCL); also elsewhere on the board
ADC_SCK: U9.13 (GPIO10_SPI1_SCK_UART1_CTS_I2C1_SDA); also elsewhere on the board
ADC_~CS0: U9.17 (GPIO14_SPI1_SCK_UART0_CTS_I2C1_SDA); also elsewhere on the board
ADC_~CS1: U9.15 (GPIO12_SPI1_RX_UART0_TX_I2C0_SDA); also elsewhere on the board
D/C: J8.13 (NWR_SCL), R54.2, U9.38 (GPIO26/ADC0_SPI1_SCK_UART1_CTS_I2C1_SDA)
GND: C64.2, C65.1, C66.1, C67.1, C68.2, C69.2, C70.2, D7.2 (GND), J5.A1 (GND), J5.A12 (GND), J5.B1 (GND), J5.B12 (GND), J6.3, J8.1 (GND), J8.2 (GND), J8.4 (GND), J8.6 (VSYNC), J8.7 (HSYNC), J8.8 (EN), J8.9 (DOTCLK), J8.17 (D0), J8.18 (D1), J8.19 (D2), J8.20 (D3), J8.21 (D4), J8.22 (D5), J8.23 (D6), J8.24 (D7), J8.25 (D8), J8.26 (D9), J8.27 (D10), J8.28 (D11), J8.29 (D12), J8.30 (D13), J8.31 (D14), J8.32 (D15), J8.33 (D16), J8.34 (D17), R33.2, R38.1, R42.1, R43.1, R44.1, R45.1, R46.1, R50.1, R53.1, R58.1, SW1.1 (A), SW2.1 (A), U9.19 (TESTEN), U11.4 (GND); also elsewhere on the board
IN1: U9.30 (GPIO19_SPI0_TX_UART0_RTS_I2C1_SCL); also elsewhere on the board
IN2: U9.31 (GPIO20_SPI0_RX_UART1_TX_I2C0_SDA); also elsewhere on the board
I_{Drive}: U9.39 (GPIO27/ADC1_SPI1_TX_UART1_RTS_I2C1_SCL); also elsewhere on the board
MISO: R49.1, R54.1, U9.2 (SPI_{0}_RX)
MOSI: J8.12 (SDI), U9.5 (GPIO3_SPI0_TX_UART0_RTS_I2C1_SCL)
unnamed: D8.2 (BK), R41.1
unnamed: D8.4 (GK), R40.1
unnamed: D8.1 (RK), R39.1
unnamed: C64.1, J5.S1 (SHIELD), R33.1
unnamed: J6.1, U9.24 (SWCLK)
unnamed: J6.2, U9.25 (SWD)
unnamed: J7.1, U9.18 (GPIO15_SPI1_TX_UART0_RTS_I2C1_SCL)
unnamed: J7.2, U9.27 (GPIO16_SPI0_RX_UART0_TX_I2C0_SDA)
unnamed: J7.3, U9.28 (GPIO17_SPI0_CSn_UART0_RX_I2C0_SCL)
unnamed: J7.4, U9.29 (GPIO18_SPI0_SCK_UART0_CTS_I2C1_SDA)
unnamed: J8.45 (IM0), R58.2
unnamed: J8.44 (IM1), R56.2
unnamed: J8.43 (IM2), R57.2
unnamed: J8.42 (IM3), R55.2
unnamed: J8.49 (LEDK1), R53.2
unnamed: J8.48 (LEDK2), R50.2
unnamed: J8.47 (LEDK3), R46.2
unnamed: J8.46 (LEDK4), R45.2
unnamed: J8.35 (SDO), R49.2
unnamed: J8.39 (XL), R51.2
unnamed: J8.41 (XR), R52.2
unnamed: J8.40 (YD), R48.2
unnamed: J8.38 (YU), R47.2
unnamed: C66.2, R34.1, SW1.2 (B), U9.26 (RUN)
unnamed: R37.2, SW2.2 (B)
unnamed: R39.2, U9.7 (GPIO5_SPI0_CSn_UART1_RX_I2C0_SCL)
unnamed: R40.2, U9.8 (GPIO6_SPI0_SCK_UART1_CTS_I2C1_SDA)
unnamed: R41.2, U9.9 (GPIO7_SPI0_TX_UART1_RTS_I2C1_SCL)
unnamed: C67.2, U9.20 (XIN), Y1.1
unnamed: C68.1, U9.21 (XOUT), Y1.2
RST: J8.11 (RST), U9.6 (GPIO4_SPI0_RX_UART1_TX_I2C0_SDA)
SCK: J8.10 (DNC_SCL), U9.4 (SPI_{0}_SCK)
SNSOUT: U9.34 (GPIO22_SPI0_SCK_UART1_CTS_I2C1_SDA); also elsewhere on the board
~CS: J8.15 (NCS), U9.3 (GPIO_{1})
~FAULT: U9.35 (GPIO23_SPI0_TX_UART1_RTS_I2C1_SCL); also elsewhere on the board
~SLEEP: U9.32 (GPIO21_SPI0_CSn_UART1_RX_I2C0_SCL); also elsewhere on the board

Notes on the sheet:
Pin 13 is D/C pin and needs to be connected to a spare pin Attach to GPIO 26
Unused

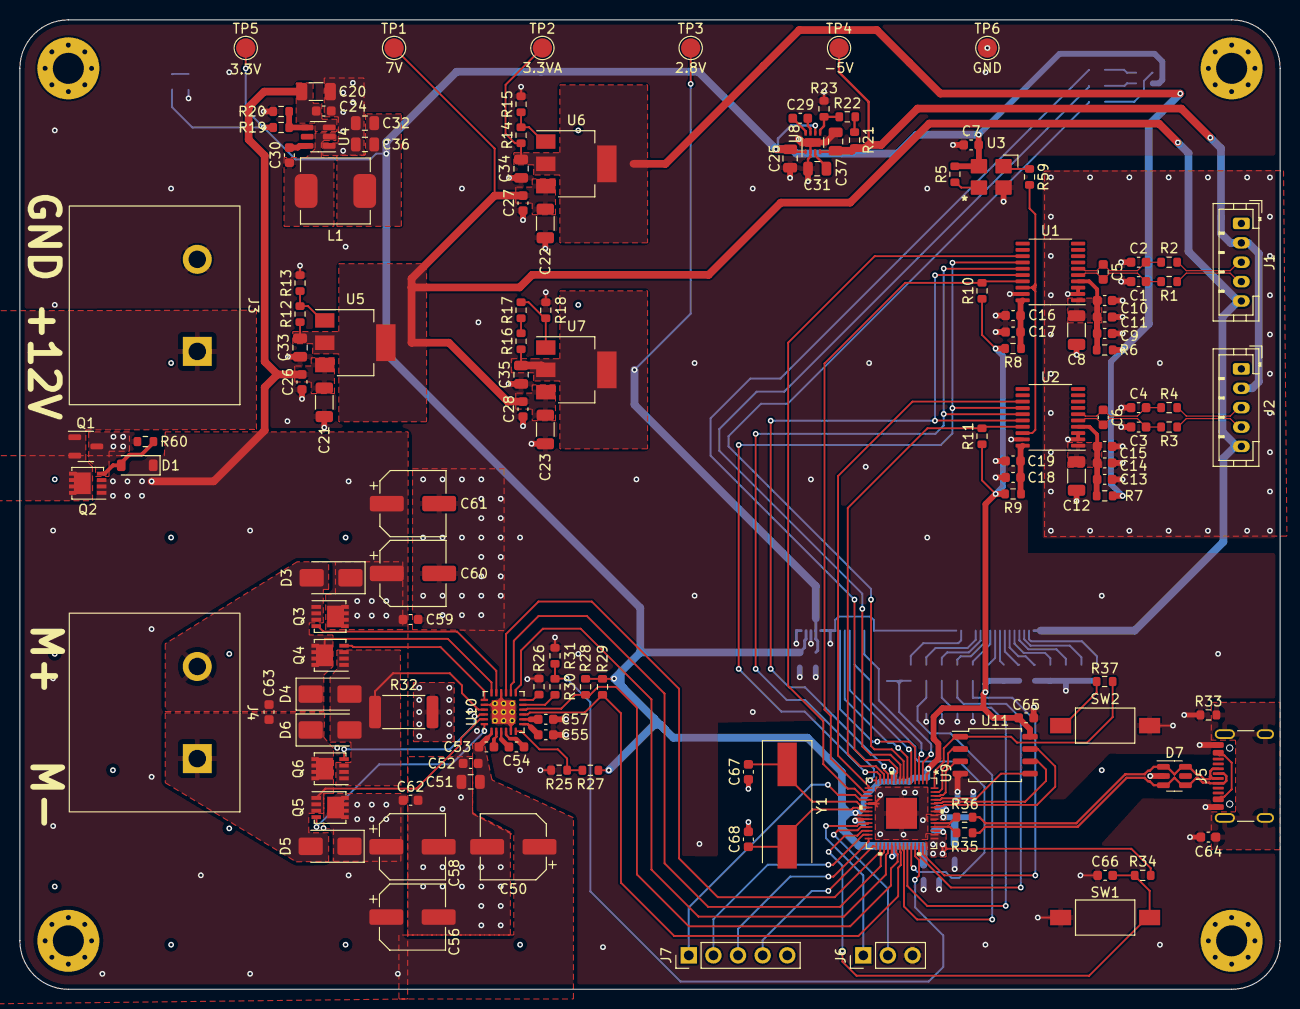
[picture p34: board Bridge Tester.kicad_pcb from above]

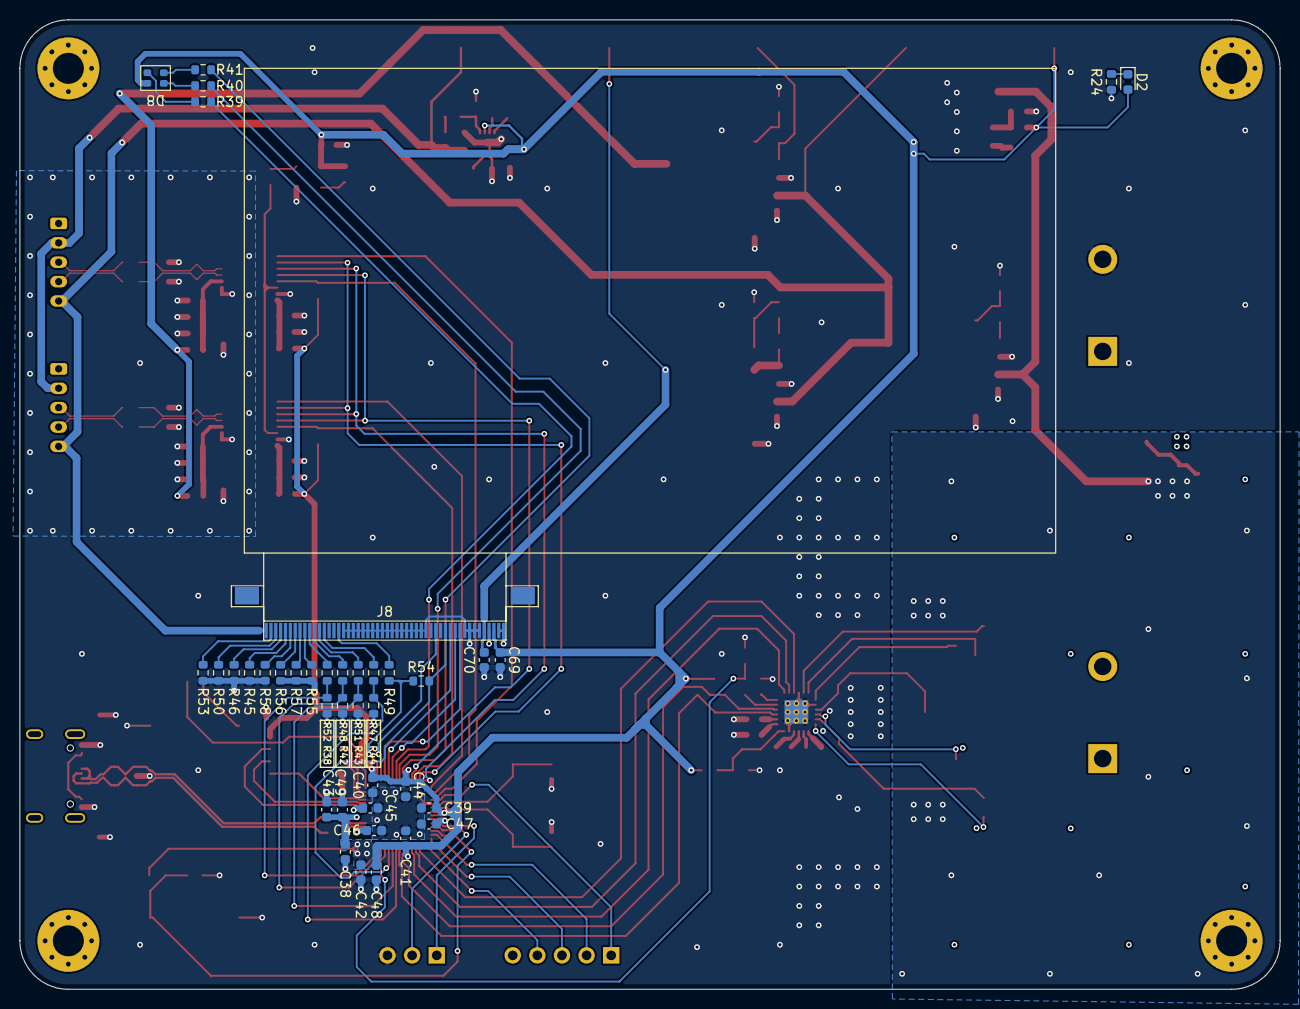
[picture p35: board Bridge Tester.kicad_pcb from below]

Board: 4 copper layers, 130.0 x 100.0 mm, 173 parts (39 on the bottom side), 116 nets.

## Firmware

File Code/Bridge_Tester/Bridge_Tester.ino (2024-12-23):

/*
This code is to control the bridge crusher








notes:


*/

#include "SPI.h"               //display and 24 bit ADCs
#include "Adafruit_GFX.h"      //display
#include "Adafruit_ILI9341.h"  //display
#include <SingleFileDrive.h>   //logged data
#include <LittleFS.h>          //logged data - no longer used
#include <EEPROM.h>            //Setting Storage
#include "pico/mutex.h"

#include <PID_v1.h>
#include "RPi_Pico_TimerInterrupt.h"  //not used at the moment

//Motor Driver Pin Defs
#define IN1 19     //pwm1
#define IN2 20     //pwm2
#define NSleep 21  //motor controller sleep
#define NFault 23  //fault ouput from controller
#define SNSOut 22  //current chop active
#define IDrive 27  //Current Readout

//Display Pin Defs
#define Display_MISO 0  //display miso line
#define Display_CS 1    //display chip select
#define Display_SCK 2   //display clock line
#define Display_MOSI 3  //display mosi line
#define Display_RST 4   //display reset
#define Display_DC 26   //DC is used for data direction control
//Display Touch Screen
//digital pins only
#define Display_X_Plus 24  //used for touch screen
#define Display_Y_Plus 25  //used for touch screen
//analog pos readout
#define Display_X_Minus 28  //used for touch screen
#define Display_Y_Minus 29  //used for touch screen

//RGB LED
#define LED_Red 7
#define LED_Green 5
#define LED_Blue 6

//ADC
#define ADC_MISO 8
#define ADC_MOSI 11
#define ADC_SCK 10
#define ADC_CS0 14
#define ADC_CS1 12
#define ADC_IRQ0 13
#define ADC_IRQ1 9

//Screens
#define MENU 0
#define SETUP_MENU 1
#define PARAMETERS 2
#define TEST_MENU 3

//EEPROM Locations
#define EEPROM_SETUP_SPEED 0
#define EEPROM_SETUP_PRELOAD 1
#define EEPROM_SETUP_LOAD_RATE 2

bool Active = 1;
bool Change_Dir = 0;
uint8_t SPEED = 255;
bool DIR = 0;
uint16_t Current_Timer = 0;
uint16_t Touch_Counter = 0;
uint16_t Vboost = 0;
bool okayToWrite = true;
uint8_t Screen = MENU;  //

int Setup_Speed = 255;                             //just a range for the motor speed
int Setup_Preload = 5;                             //The real value is * .1 so if = 51 then 51 = 5.1
volatile int LoadL, LoadR;                         //The real value is * .1 so if = 51 then 51 = 5.1
volatile int Tare_LoadL = 370, Tare_LoadR = 1040;  //The real value is * .1 so if = 51 then 51 = 5.1
double Load_Rate = 5;
volatile double Working_LoadL = 0, Working_LoadR = 0, Pass_LoadL, Pass_LoadR;
volatile bool Load_Updatable = 1;

volatile bool ADC_Read_Value_Flag0 = 0, ADC_Read_Value_Flag1 = 0;
volatile bool ADC_Busy = 0;

volatile double Max_Load = 0;
volatile double Load = 0;
uint32_t Elapsed_Time = 0;  //second since test start
volatile bool Test_Active = 0;
volatile bool Test_State = 0;  //1 if finished



Adafruit_ILI9341 Display = Adafruit_ILI9341(Display_CS, Display_DC, Display_RST);

mutex_t myMutex;

void setup() {
  // put your setup code here, to run once:

  //15 right bar
  //28 top bar
  //27 left bar
  //26 bottom bar
  Serial.begin(115200);
  mutex_init(&myMutex);
  //LittleFS.begin();
  SPI.setRX(Display_MISO);
  SPI.setSCK(Display_SCK);
  SPI.setTX(Display_MOSI);

  Display.initSPI(63'000'000, SPI_MODE0);
  Display.begin();
  Display.setRotation(1);

  // Set up the USB disk share

  //singleFileDrive.onDelete(deleteCSV);
  //singleFileDrive.onPlug(plug);
  //singleFileDrive.onUnplug(unplug);
  //singleFileDrive.begin("data.csv", "Bridge Tester Data.csv");

  analogReadResolution(12);

  //Motor Controller Pin defs
  pinMode(IN1, OUTPUT_2MA);     //PWM0
  pinMode(IN2, OUTPUT_2MA);     //PWM1
  pinMode(NSleep, OUTPUT_2MA);  //place the Driver into Sleep mode when Low
  pinMode(NFault, INPUT);       //Fault Active low
  pinMode(SNSOut, INPUT);       //Current Chop Active
  pinMode(IDrive, INPUT);       //Current Readout from the Shunt amplifyer


  analogWriteFreq(50'000);

  //Settings
  EEPROM.begin(512);
  Setup_Speed = EEPROM.read(EEPROM_SETUP_SPEED);
  Setup_Preload = EEPROM.read(EEPROM_SETUP_PRELOAD);
  Load_Rate = float(EEPROM.read(EEPROM_SETUP_LOAD_RATE)) * 0.1;

  delay(5000);
}
uint8_t Register_location = 0;
void loop() {
  Main_Menu();
}

#define BUFFER_SIZE 20

double bufferL[BUFFER_SIZE], bufferR[BUFFER_SIZE];  // Array to hold the samples
int bufferIndex = 0;                                // Current index in the buffer
double newValueR = 0, newValueL = 0, sumR = 0, sumL;

#define PIN_INPUT 0
#define PIN_OUTPUT 25

//Define Variables we'll be connecting to
double Setpoint, Input, Output;

//Specify the links and initial tuning parameters
double Kp = 20, Ki = 4, Kd = 5;
PID myPID(&Input, &Output, &Setpoint, Kp, Ki, Kd, DIRECT);


void setup1() {

  //ADC
  SPI1.setRX(ADC_MISO);
  SPI1.setSCK(ADC_SCK);
  SPI1.setTX(ADC_MOSI);

  SPI1.begin();

  pinMode(ADC_CS0, OUTPUT_12MA);  //cs0 is top adc
  pinMode(ADC_CS1, OUTPUT_12MA);
  pinMode(ADC_IRQ0, INPUT);
  pinMode(ADC_IRQ1, INPUT);

  //RGB LED
  pinMode(LED_Red, OUTPUT_12MA);
  pinMode(LED_Green, OUTPUT_12MA);
  pinMode(LED_Blue, OUTPUT_12MA);

  digitalWrite(LED_Red, HIGH);
  digitalWrite(LED_Green, HIGH);
  digitalWrite(LED_Blue, HIGH);


  digitalWrite(ADC_CS0, HIGH);
  digitalWrite(ADC_CS1, HIGH);

  digitalWrite(ADC_CS0, LOW);
  SPI1.beginTransaction(SPISettings(20'000'000, MSBFIRST, SPI_MODE0));
  SPI1.transfer(0b01111000);  //rst register map
  SPI_Restart(ADC_CS0);
  SPI1.transfer(0b01000110);  //write register 0x01
  SPI1.transfer(0b11100000);  //set config0 internal ref and internal clk
  SPI_Restart(ADC_CS0);
  SPI1.transfer(0b01001010);  //write register 0x02
  SPI1.transfer(0b00000000);  //set config1 amclk = mclk osr 256
  SPI_Restart(ADC_CS0);
  SPI1.transfer(0b01001110);  //write register 0x03
  SPI1.transfer(0b10100001);  //set config2 gain to 8x hardware
  SPI_Restart(ADC_CS0);
  SPI1.endTransaction();
  digitalWrite(ADC_CS0, HIGH);

  digitalWrite(ADC_CS1, LOW);
  SPI1.beginTransaction(SPISettings(20'000'000, MSBFIRST, SPI_MODE0));
  SPI1.transfer(0b01111000);  //rst register map
  SPI_Restart(ADC_CS1);
  SPI1.transfer(0b01000110);  //write register 0x01
  SPI1.transfer(0b11100000);  //set config0 internal ref and internal clk
  SPI_Restart(ADC_CS1);
  SPI1.transfer(0b01001010);  //write register 0x02
  SPI1.transfer(0b00000000);  //set config1 amclk = mclk osr 256
  SPI_Restart(ADC_CS1);
  SPI1.transfer(0b01001110);  //write register 0x03
  SPI1.transfer(0b10100001);  //set config2 gain to 8x hardware
  SPI_Restart(ADC_CS1);
  SPI1.endTransaction();
  digitalWrite(ADC_CS1, HIGH);

  for (int i = 0; i < BUFFER_SIZE; i++) {
    bufferL[i] = 0;
    bufferR[i] = 0;
  }
  myPID.SetMode(AUTOMATIC);
}


int32_t total;
uint32_t ADC_READING;
uint32_t Load_Time = 0, Last_Load_Time = 0;
uint32_t Target_Load_Update_Timer = 0, Load_Restart_Timer = 0, Start_Time_Delay = 0;


int Motor_Speed = 0;
float Active_Load_Rate = 0;
float Last_Load = 0;

double Target_Load = 0;
bool First_Time = 1;

void loop1() {

  if (Test_Active && !Test_State) {  //the test is running Test_Active && !Test_State
    Load_Time = millis();

    if (Target_Load_Update_Timer <= millis()) {
      Target_Load += Load_Rate / 100.0;
      Target_Load_Update_Timer = millis() + 10;  //update 10 times per second
    }

    //if (First_Time) {
    //  First_Time = 0;
    //  Start_Time_Delay = millis() + 10000;  //5 second wait to start
    //}


    if (Target_Load < (Working_LoadR + Working_LoadL)) {  //Active_Load_Rate > (Load_Rate)
      if (!(Motor_Speed <= 0)) {
        Motor_Speed = 0;
      }
    } else if (Target_Load > (Working_LoadR + Working_LoadL)) {
      if (!(Motor_Speed == 255)) {

        Motor_Speed++;
        if(Working_LoadR + Working_LoadL <= 70){
          delay(10);
        }
      }
    }



    Serial.println(Motor_Speed);
    Last_Load_Time = Load_Time;
    Update_Motor(Motor_Speed, 1);
    Start_Motor();

    if ((Motor_Current() < 0.1)) {  //
      if (Current_Timer >= 1000) {  //1000 cycles that the current is below threshold prevents false readings
        DIR = !DIR;
        Current_Timer = 0;
        Target_Load = 0;

        Test_State = 1;
        Test_Active = 0;
        Motor_Speed = 0;
        First_Time = 1;

        Update_Motor(255, 0);  //move motor up
        delay(100);
        while (Motor_Current() > 0.5)
          ;
      }
      Current_Timer++;
    } else {
      Current_Timer = 0;
    }

    //Update_Motor(255, 1);//needs full duty cycle to read the current
    if ((Working_LoadR >= 440) || (Working_LoadL >= 440)) {  //motor has reached end of travel
      Test_State = 1;
      Test_Active = 0;
      Motor_Speed = 0;
      Target_Load = 0;
      First_Time = 1;
      Update_Motor(255, 0);  //move motor up
      delay(100);
      digitalWrite(LED_Red, LOW);  //Set Red to indicate max load has been reached
      while (Motor_Current() > 0.5)
        ;
      Update_Motor(0, 0);
      Stop_Motor();

    } else if ((Test_State && !Test_Active) && Screen == TEST_MENU) {  //end test
      Motor_Speed = 0;
      digitalWrite(LED_Green, LOW);  //Set Green Test has ended
      Update_Motor(0, 0);
      Stop_Motor();
    }
  } else if ((Test_State || !Test_Active) && Screen == TEST_MENU) {
    Load_Time = millis();
    Last_Load_Time = Load_Time;
    Update_Motor(0, 0);
    Stop_Motor();
  }

  if (!ADC_Busy) {
    delay(1);            //
    ADC_Take_Reading();  //gets the adc value from the adc register
  }

  if (ADC_Read_Value_Flag0 && ADC_Read_Value_Flag1) {

    total = Get_ADC_Register(0, 0);
    while (!Load_Updatable)
      ;
    Load_Updatable = 0;

    if (bitRead(total, 23)) {
      ADC_READING = (~((total) | (0b11111111000000000000000000000000))) + 1;
    } else {
      ADC_READING = total;
    }
    ADC_READING = ADC_READING * 1.17;  //Input impedance compensation two values because of the use of the use of the interal clk
    newValueR = (float(ADC_READING) / 1264);

    total = Get_ADC_Register(1, 0);

    if (bitRead(total, 23)) {
      ADC_READING = (~((total) | (0b11111111000000000000000000000000))) + 1;
    } else {
      ADC_READING = total;
    }
    ADC_READING = ADC_READING * 1.3714;  //Input impedance compensation two values because of the use of the use of the interal clk
    newValueL = (float(ADC_READING) / 1264);

    ADC_Read_Value_Flag0 = 0;
    ADC_Read_Value_Flag1 = 0;
    ADC_Busy = 0;  //clear ADC busy flag

    //LoadL = int(newValueL * 10);
    //LoadR = int(newValueR * 10);

    /////////////////////
    sumR -= bufferR[bufferIndex];      // Subtract the oldest value from the sum
    bufferR[bufferIndex] = newValueR;  // Replace the oldest value with the new value
    sumR += newValueR;                 // Add the new value to the sum

    sumL -= bufferL[bufferIndex];      // Subtract the oldest value from the sum
    bufferL[bufferIndex] = newValueL;  // Replace the oldest value with the new value
    sumL += newValueL;                 // Add the new value to the sum

    bufferIndex = (bufferIndex + 1) % BUFFER_SIZE;

    //if(bufferIndex >= BUFFER_SIZE){
    //  bufferIndex = 0;
    //}else{
    //  bufferIndex++;
    //}

    // Calculate the rolling average
    Working_LoadR = sumR / BUFFER_SIZE;
    Working_LoadL = sumL / BUFFER_SIZE;

    mutex_enter_blocking(&myMutex);  // Lock the mutex

    Working_LoadR = Working_LoadR - (Tare_LoadR * 0.1);
    Working_LoadL = Working_LoadL - (Tare_LoadL * 0.1);

    Pass_LoadL = Working_LoadL;
    Pass_LoadR = Working_LoadR;
    mutex_exit(&myMutex);

    Load_Updatable = 1;
  }
}


//Main_Menu();
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

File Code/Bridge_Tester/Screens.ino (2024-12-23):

////////////////////////////////////////////////////////////////////////////////////////

void Main_Menu() {
  Display.fillScreen(0);  //clear screen

  //header
  Display.setCursor(48, 5);
  Display.setTextColor(ILI9341_WHITE);
  Display.setTextSize(3);
  Display.print("Bridge Tester");
  Display.setTextSize(1);
  Display.setCursor(285, 2);
  Display.println("V1.00");

  //Test Button
  Display.fillRoundRect(32, 170, 256, 50, 8, ILI9341_DARKGREEN);
  Display.setCursor(125, 185);
  Display.setTextSize(3);
  Display.setTextColor(ILI9341_WHITE);
  Display.print("TEST");

  //Setup Button
  Display.fillRoundRect(32, 40, 256, 50, 8, ILI9341_BLUE);
  Display.setCursor(115, 55);
  Display.setTextSize(3);
  Display.setTextColor(ILI9341_WHITE);
  Display.print("Setup");

  //Parameters Button
  Display.fillRoundRect(32, 105, 256, 50, 8, ILI9341_BLUE);
  Display.setCursor(75, 118);
  Display.setTextSize(3);
  Display.setTextColor(ILI9341_WHITE);
  Display.print("Parameters");

  uint8_t Touch_OBJ = 0;
  Screen = MENU;

  delay(100);

  bool Filled1 = 0, Filled2 = 0, Filled3 = 0;

  while (Screen == MENU) {
    if (Check_Box_Touch(32, 40, 256, 50, 5, 100)) {  //Check_Box_Touch(32, 40, 256, 50, 5, 100)
      if (!Filled1) {
        Display.fillRoundRect(10, 60, 12, 12, 6, Display.color565(0, 150, 50));
        Display.fillRoundRect(10, 190, 12, 12, 6, Display.color565(0, 0, 0));
        Display.fillRoundRect(10, 125, 12, 12, 6, Display.color565(0, 0, 0));
        Filled1 = 1;
        Filled2 = 0;
        Filled3 = 0;
      }
      Screen = SETUP_MENU;
      Setup_Menu();
    } else if (Check_Box_Touch(32, 105, 256, 50, 5, 100)) {  //Check_Box_Touch(32, 105, 256, 50, 5, 100)
      if (!Filled2) {
        Display.fillRoundRect(10, 125, 12, 12, 6, Display.color565(0, 150, 50));
        Display.fillRoundRect(10, 190, 12, 12, 6, Display.color565(0, 0, 0));
        Display.fillRoundRect(10, 60, 12, 12, 6, Display.color565(0, 0, 0));

        Filled1 = 0;
        Filled2 = 1;
        Filled3 = 0;
        Screen = PARAMETERS;
        Parameters_Menu();
      }
    } else if (Check_Box_Touch(32, 170, 256, 50, 5, 100)) {  //Check_Box_Touch(32, 170, 256, 50, 5, 100)
      if (!Filled3) {
        Display.fillRoundRect(10, 190, 12, 12, 6, Display.color565(0, 150, 50));
        Display.fillRoundRect(10, 60, 12, 12, 6, Display.color565(0, 0, 0));
        Display.fillRoundRect(10, 125, 12, 12, 6, Display.color565(0, 0, 0));
        Filled1 = 0;
        Filled2 = 0;
        Filled3 = 1;
      }
      Screen = TEST_MENU;
      Test_Menu();
    } else {
      Display.fillRoundRect(10, 170, 12, 12, 6, Display.color565(0, 0, 0));
      Display.fillRoundRect(10, 40, 12, 12, 6, Display.color565(0, 0, 0));
      Display.fillRoundRect(10, 105, 12, 12, 6, Display.color565(0, 0, 0));
    }
  }
}

////////////////////////////////////////////////////////////////////////////////////////////////////////////////////////////
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

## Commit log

2024-12-23 Add files via upload
    CAD upload
    [Bottom Plate.FCStd, Bridge Tester ASM.FCStd, E-STOP.FCStd, Power Supply.FCStd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]
2024-12-23 Add files via upload
    Kicad Upload
    [Block Diagram.kicad_sch, Bridge Tester.kicad_pcb, Load Cell Acquisition System.kicad_sch, Motor Driver.kicad_sch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]
